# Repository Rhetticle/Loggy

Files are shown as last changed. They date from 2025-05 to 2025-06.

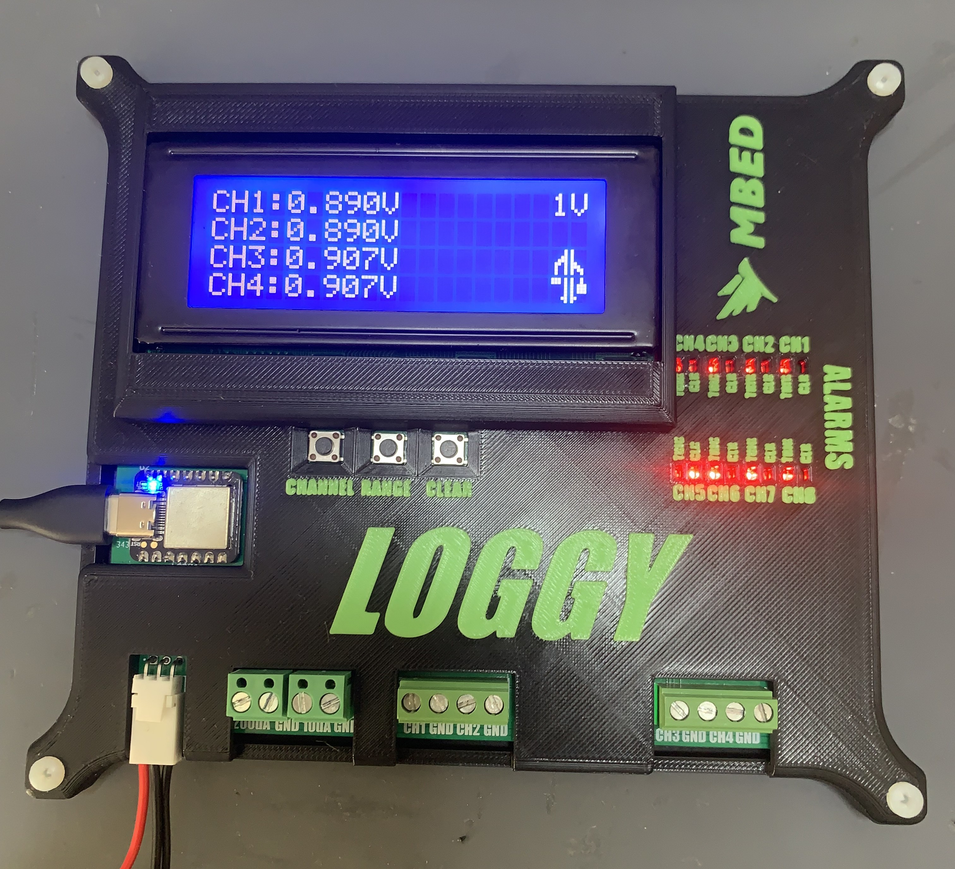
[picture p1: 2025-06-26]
Images/image5.jpeg

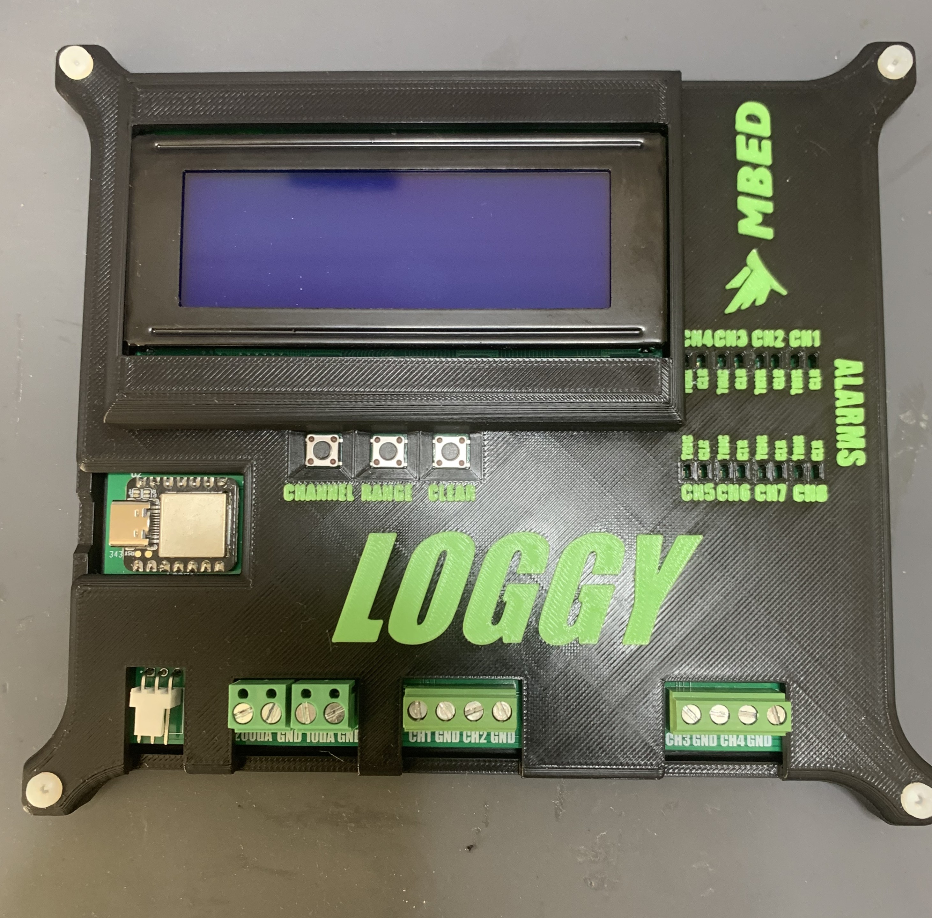
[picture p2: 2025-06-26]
Images/image4.jpeg

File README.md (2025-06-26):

# Loggy
## Four input channel data acquisition device as part of UQ's ENGG2800 Team Project 1 course.



## Overview
Loggy is a four input channel data acquisition device operating at 168 Samples/second with input channels being rated to +/- 12V. Loggy also has four extra channel (CH5 -> CH8) with CH5,CH6,CH7 being the x,y,z acceleration values from the on board accelerometer respectively and CH8 being the ambient temperature. Loggy also features two on board current sources (10uA and 200uA) accurate to +/- 5% for general use (e.g. using with resistive temperature sensors).

Loggy features a simple on board alarm system which monitors the eight channels to see if any go beyond a configurable range (alarm threshold). 16 red LEDs (2 per channel) are used to indicate whether an alarm has occured or not for a given channel. Loggy allows alarms to be in one of three modes; disabled, live (alarm status updated repeatedly) or latching (triggered LED stays latched permenantly once threshold is breached). 

As part of the project a complete GUI was required which would interface to the device via USB to allow users to view live data from their computer as well as configure the device (See "Software" section below for more info). All measurements made by Loggy are also shown on a 20x4 LCD along with alarm statuses and range setting.

## Standards and Requirements
The Loggy device and software was required to comply with mock standards (known as "TP-Standards") to mimic real-world standard compliance. All teams were required to comply with 152 individual standards relating to things such as PCB layout and design, schematic layout and design, software design etc.

The Loggy device and software also had multiple extra requirements on top of the TP-Standards. These requirements included:

* All input channels must be rated for +/- 11V regardless of the range setting
* The entire device must have a BOM of $100 or less
* The GUI must never crash
* Current sources must be accurate to +/- 5%
* Input channel readings must be accurate to +/- 2.5%
* ADCs used must be 16-bit resolution or higher
* All eight channels must be sampled within a 100ms window
* Sample rate must be at least 2 Samples/second

## Hardware
All hardware design was done by Rhett Humphreys. This included designing the digital sections of the device such as the ADCs, MCU, alarm LED driver etc. as well as the analog sections such as the input circuitry for the four input channels. It also included the layout, routing and assembly of the PCB.

The PCB is a standard 2 layer board 1.6mm thick with a 3V3 pour on the top layer and a GND pour on the bottom layer. Surface mount components were preferred in order to stay under the $100 BOM limit. 

## Firmware
Firmware was written by Zhe Gao. This included writing low level drivers for on board devices such as the ADCs, accelerometers and LED driver for alarms as well combining these drivers within the application code for Loggy.

## Software
The GUI software was jointly written by Luke Pidgeon and Sithika Mannakkara. The GUI was written in python and allows the user to view live plots of data read by Loggy as well as configure parameters of the device such as alarm thresholds and alarm types.
### Controls
The controls panel allows the user to connect to the Loggy device as well as perform other actions such as enabling/disabling different plots, changing the voltage range and choosing to begin recording data.
GUI Controls
### Settings
The settings panel allows the user to configure parameters stored on the Loggy device itself such as alarm thresholds and alarm types as well as other GUI parameters such as number of sample points to use for plots, plot scale etc. It also allows the user to configure a voltage channel to be used as a resistive temperature device (RTD) mode.
GUI Settings
### Plots
The plots panel shows the current live plots and allows user to read sampled value by hovering their mouse over the plots
GUI Plots
### Replay
The replay panel allows users to replay/view a data recording previously made. Recorded data is saved as a csv file which can then be imported into the GUI for viewing and also allows users to view the value of samples similar to the live plots.
GUI Replay

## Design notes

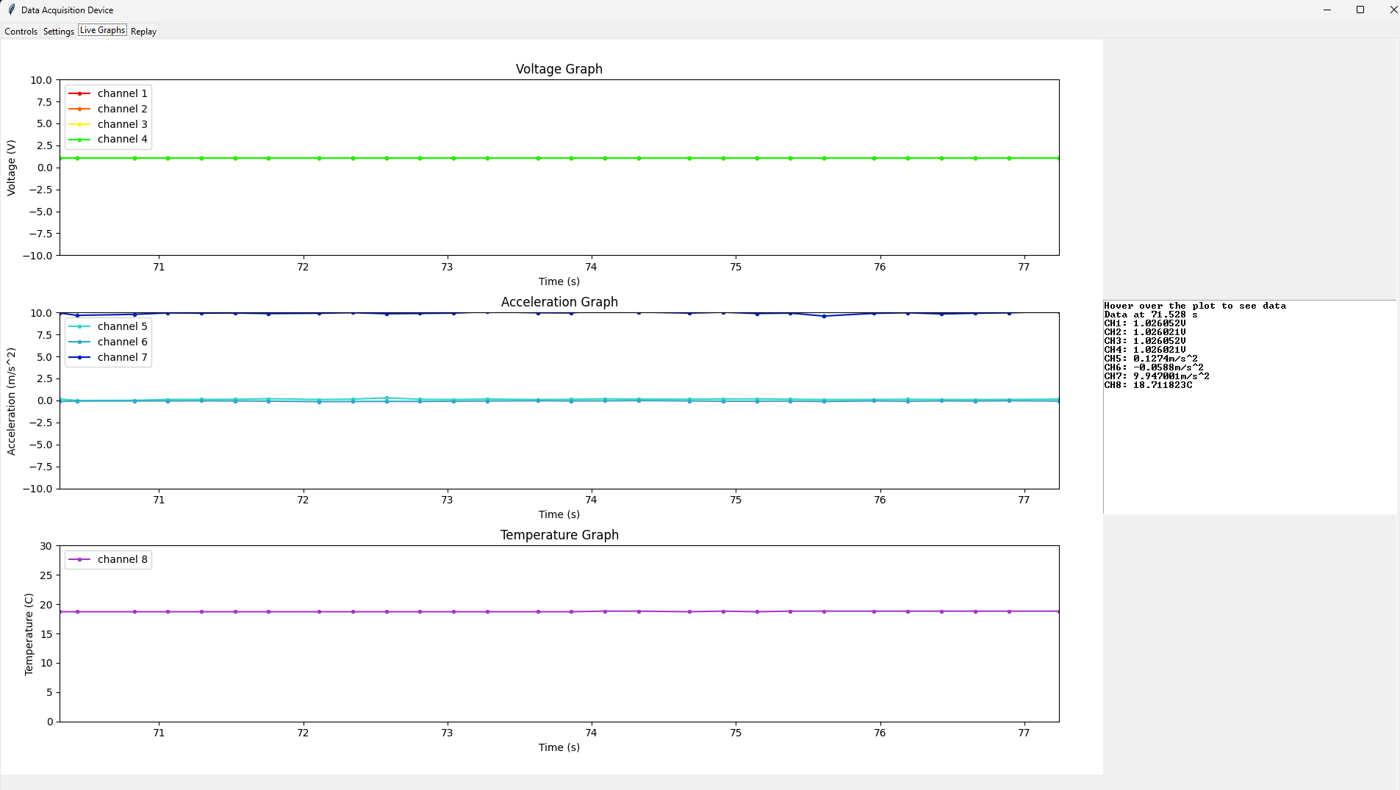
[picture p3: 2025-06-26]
Images/GUI Plots.png

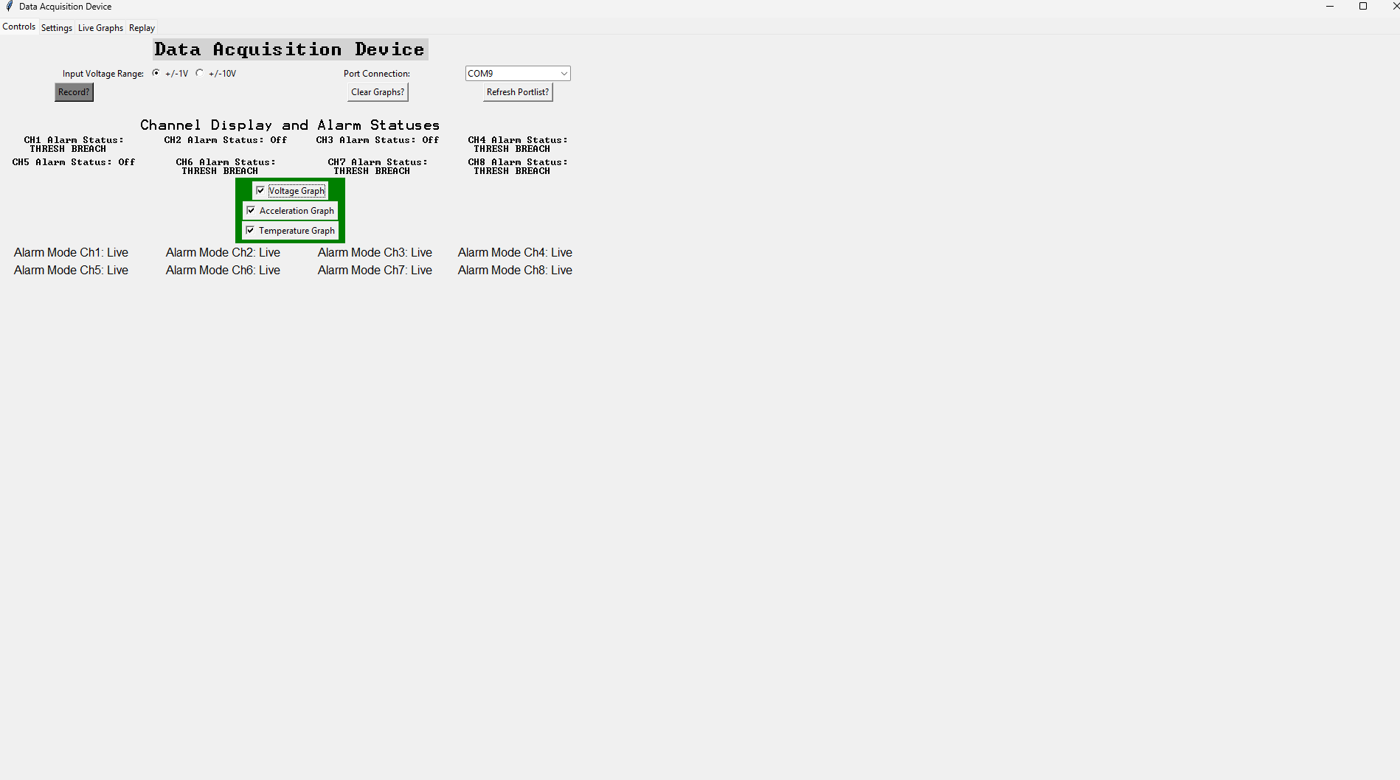
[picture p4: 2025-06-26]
Images/GUI Controls.png

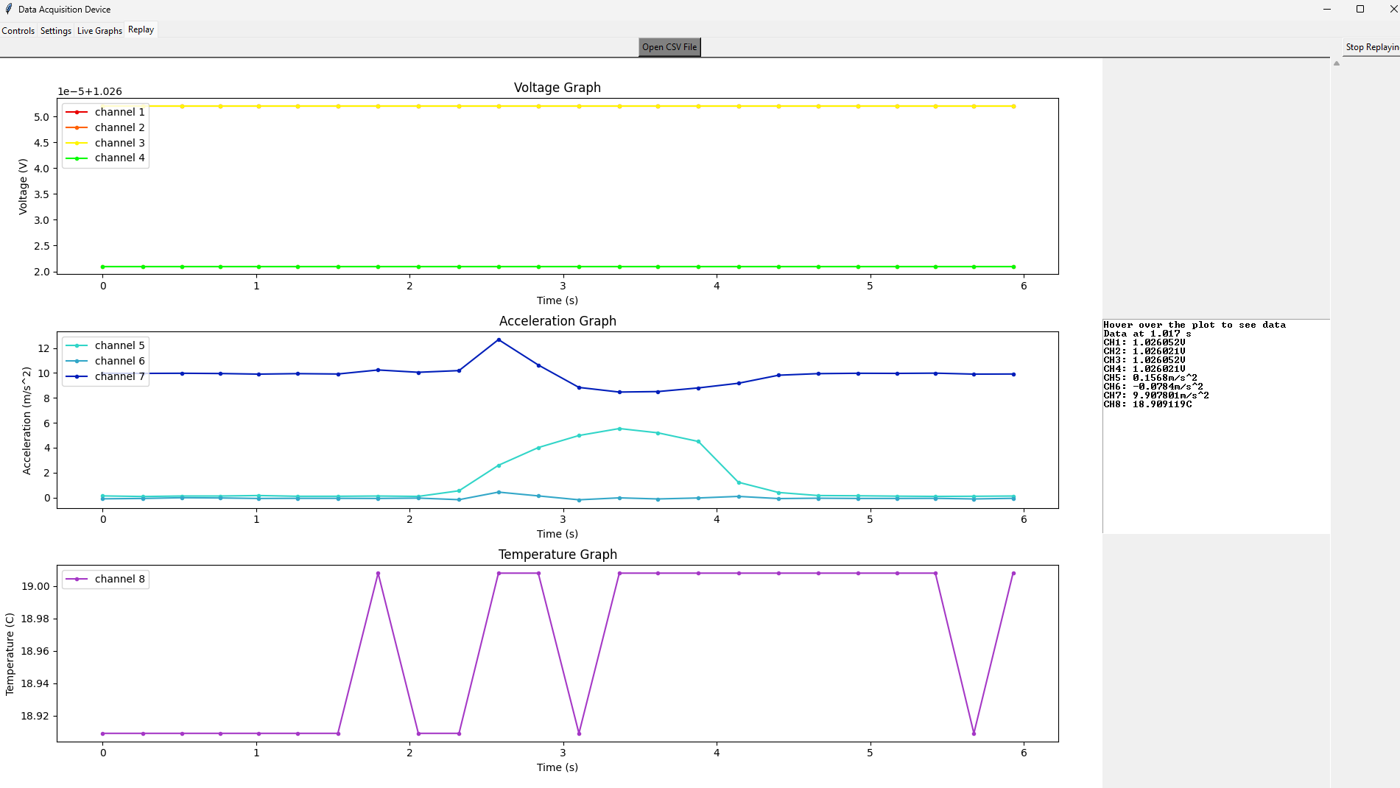
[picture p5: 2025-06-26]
Images/GUI Replay.png

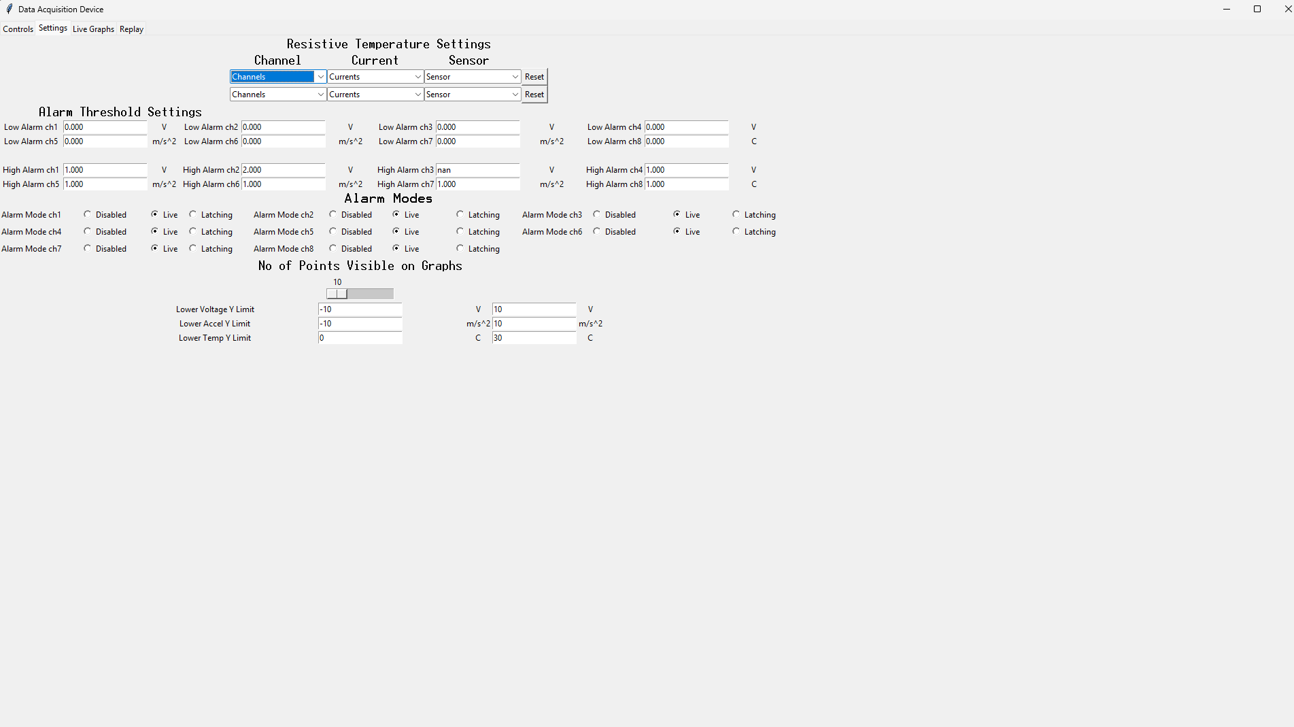
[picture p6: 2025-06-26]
Images/GUI Settings.png

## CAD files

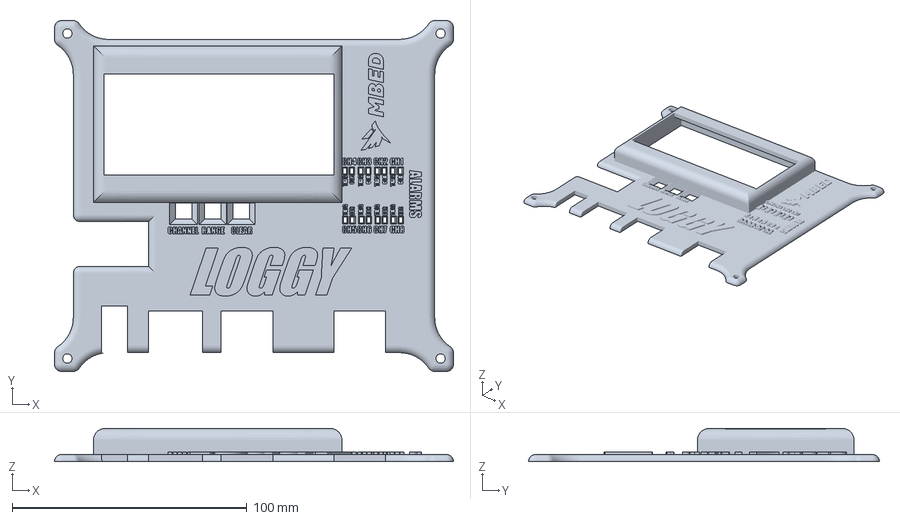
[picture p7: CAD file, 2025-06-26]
STL/Loggy Top Proj.3mf
170.0 x 149.5 x 14.1 mm

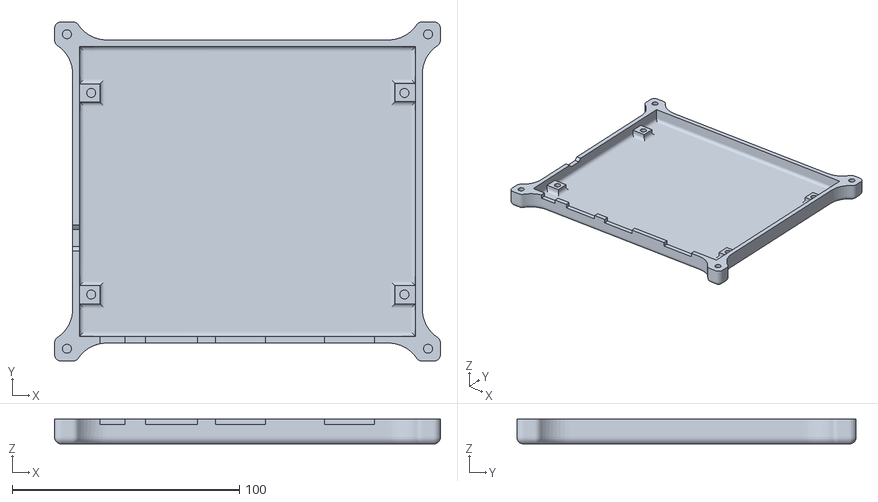
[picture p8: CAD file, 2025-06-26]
STL/Loggy Bottom.stl
170.0 x 149.5 x 11.0

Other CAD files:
STL/Loggy Top.stl

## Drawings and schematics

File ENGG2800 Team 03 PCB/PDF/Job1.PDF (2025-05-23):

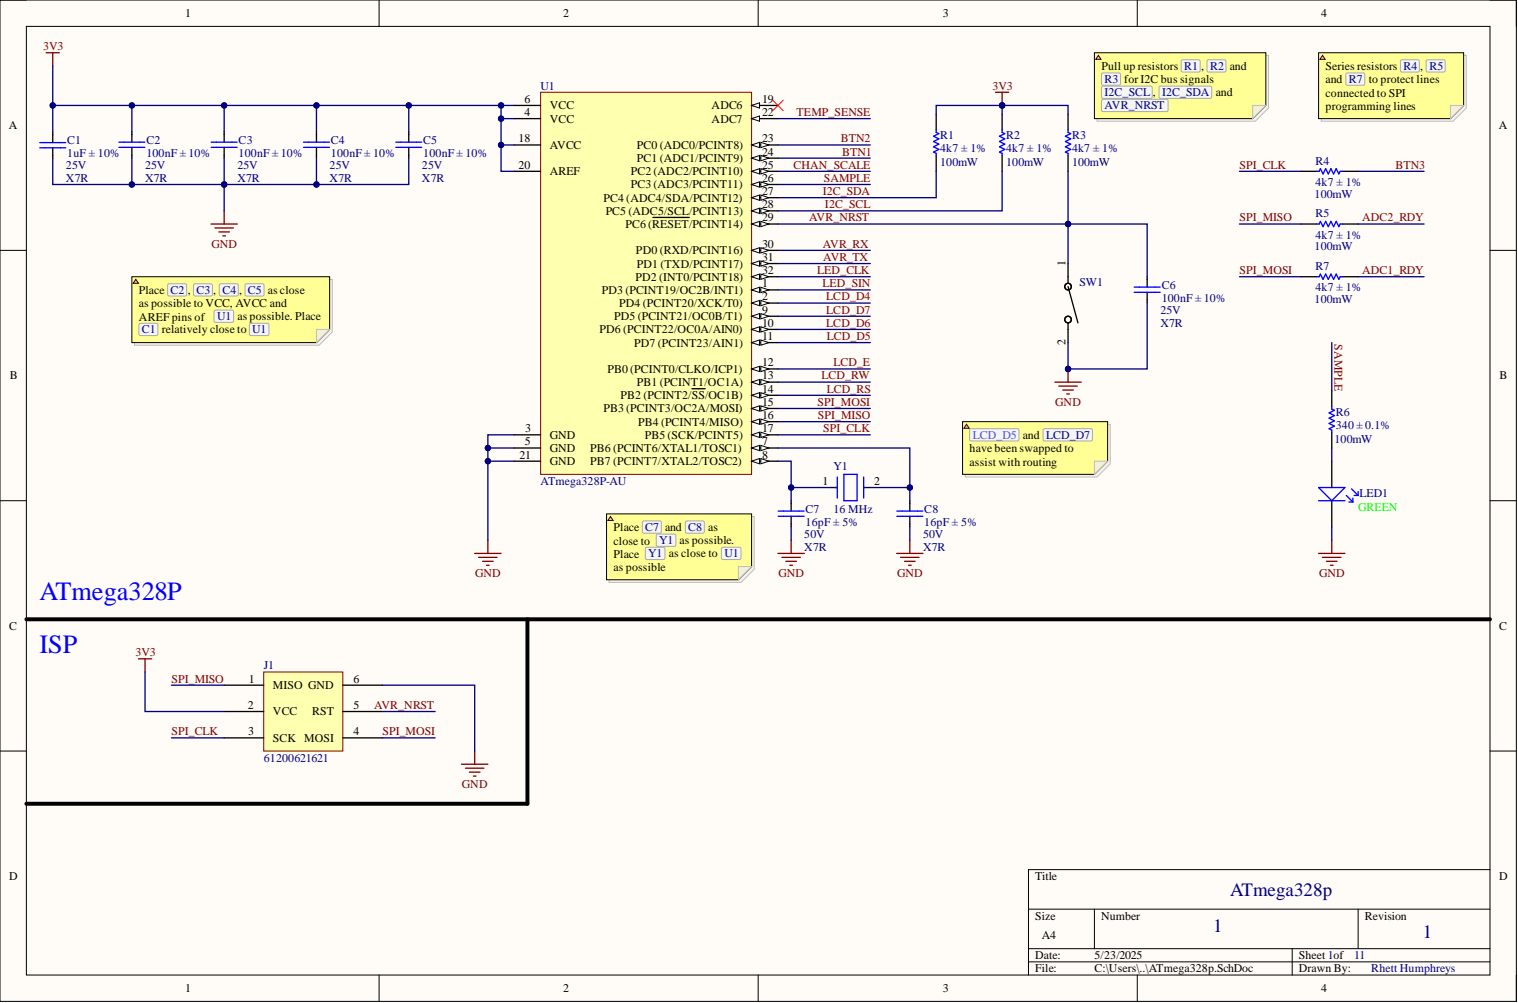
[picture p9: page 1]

2 6 2 7 | SAMPL E I2C_ S D A

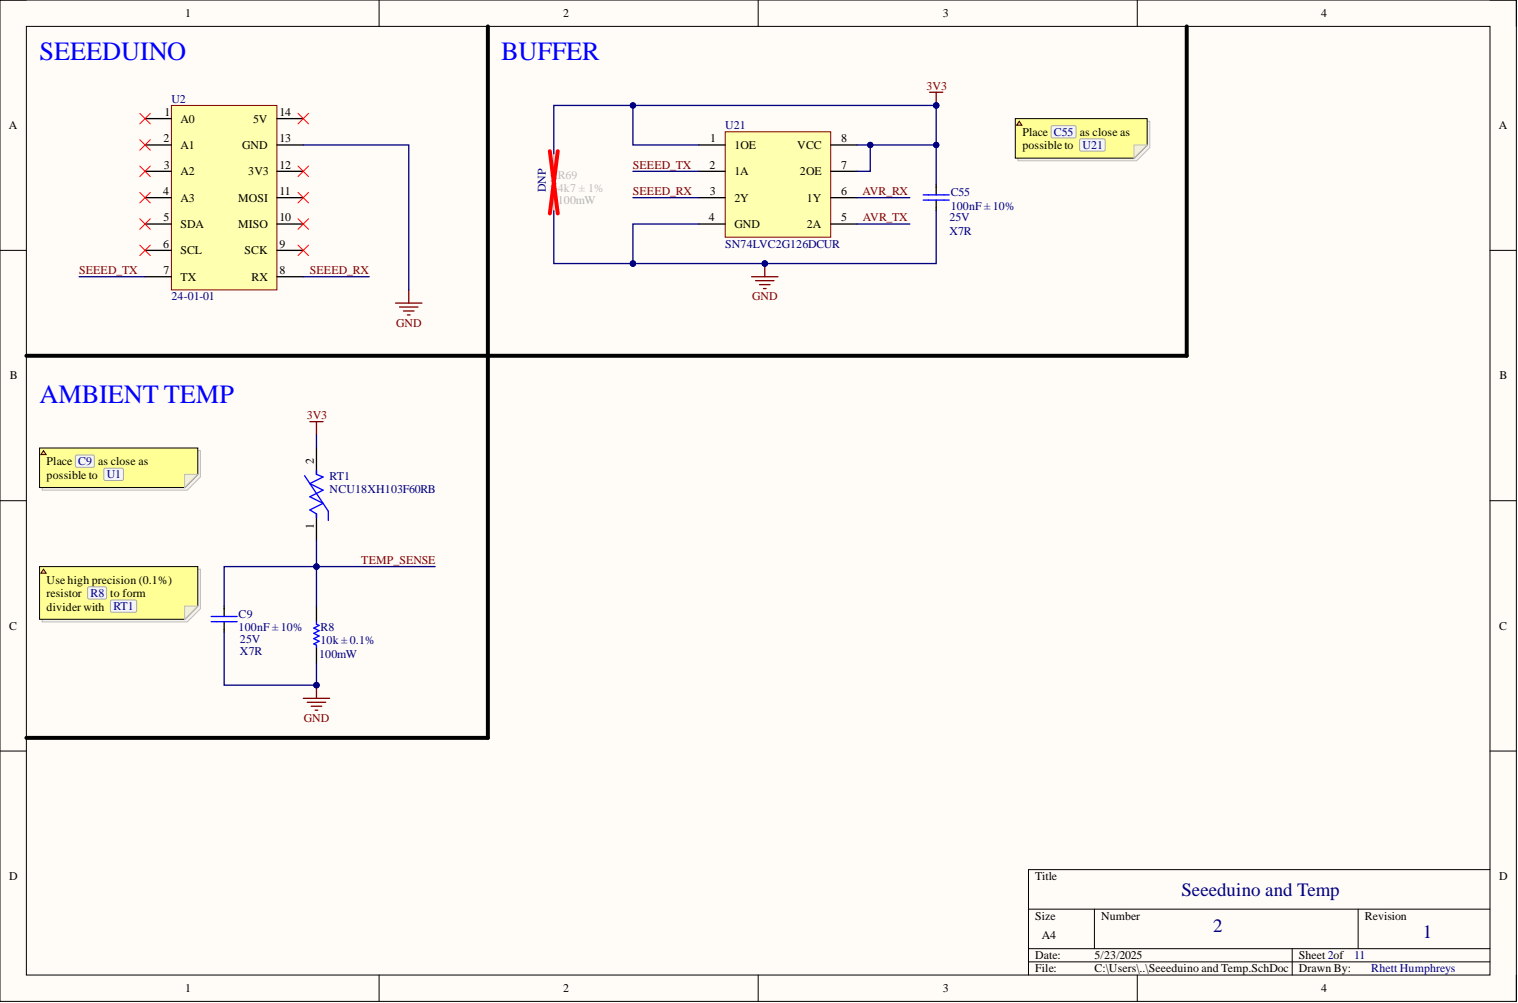
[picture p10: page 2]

Place C55 as close as
possible to U21

Place C9 as close as
possible to U1

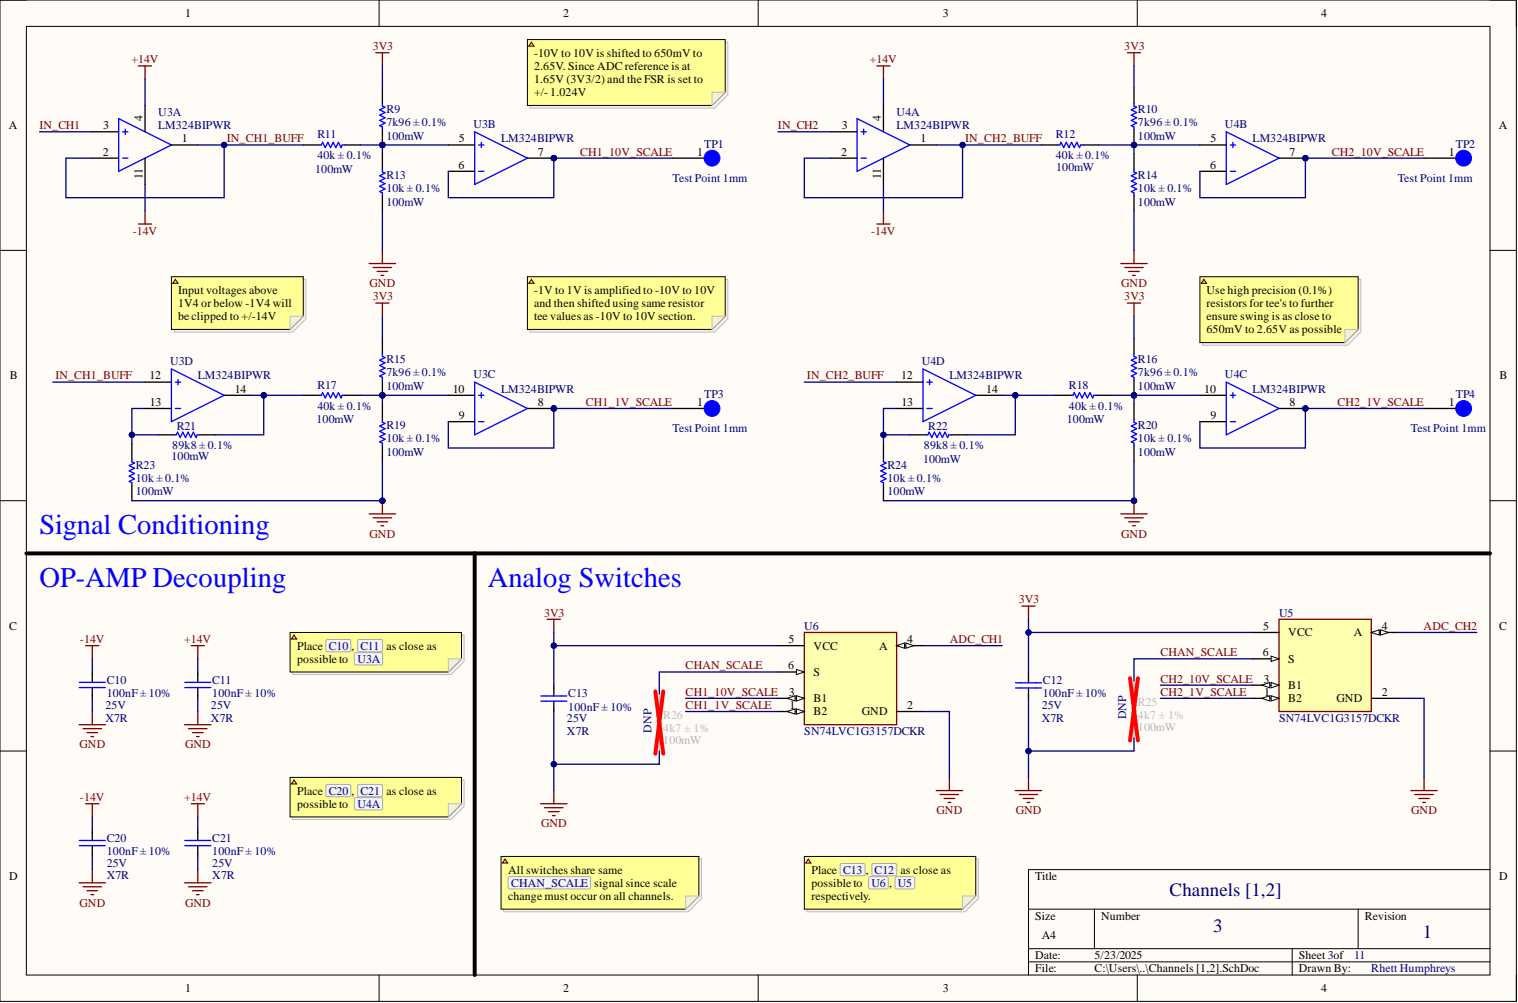
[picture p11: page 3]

-10V to 10V is shifted to 650mV to
2.65V. Since ADC reference is at
1.65V (3V3/2) and the FSR is set to

-1V to 1V is amplified to -10V to 10V
and then shifted using same resistor
tee values as -10V to 10V section.

Use high precision (0.1%)
resistors for tee'sto further
ensure swing is as close to
650mV to 2.65V as possible

Place C10 , C11 as close as
possible to U3A

Place C20 , C21 as close as
possible to U4A

All switches share same
CHAN_SCALE signalsince scale
change must occur on all channels.

Place C13 , C12 as close as
possible to U6 , U5
respectively.

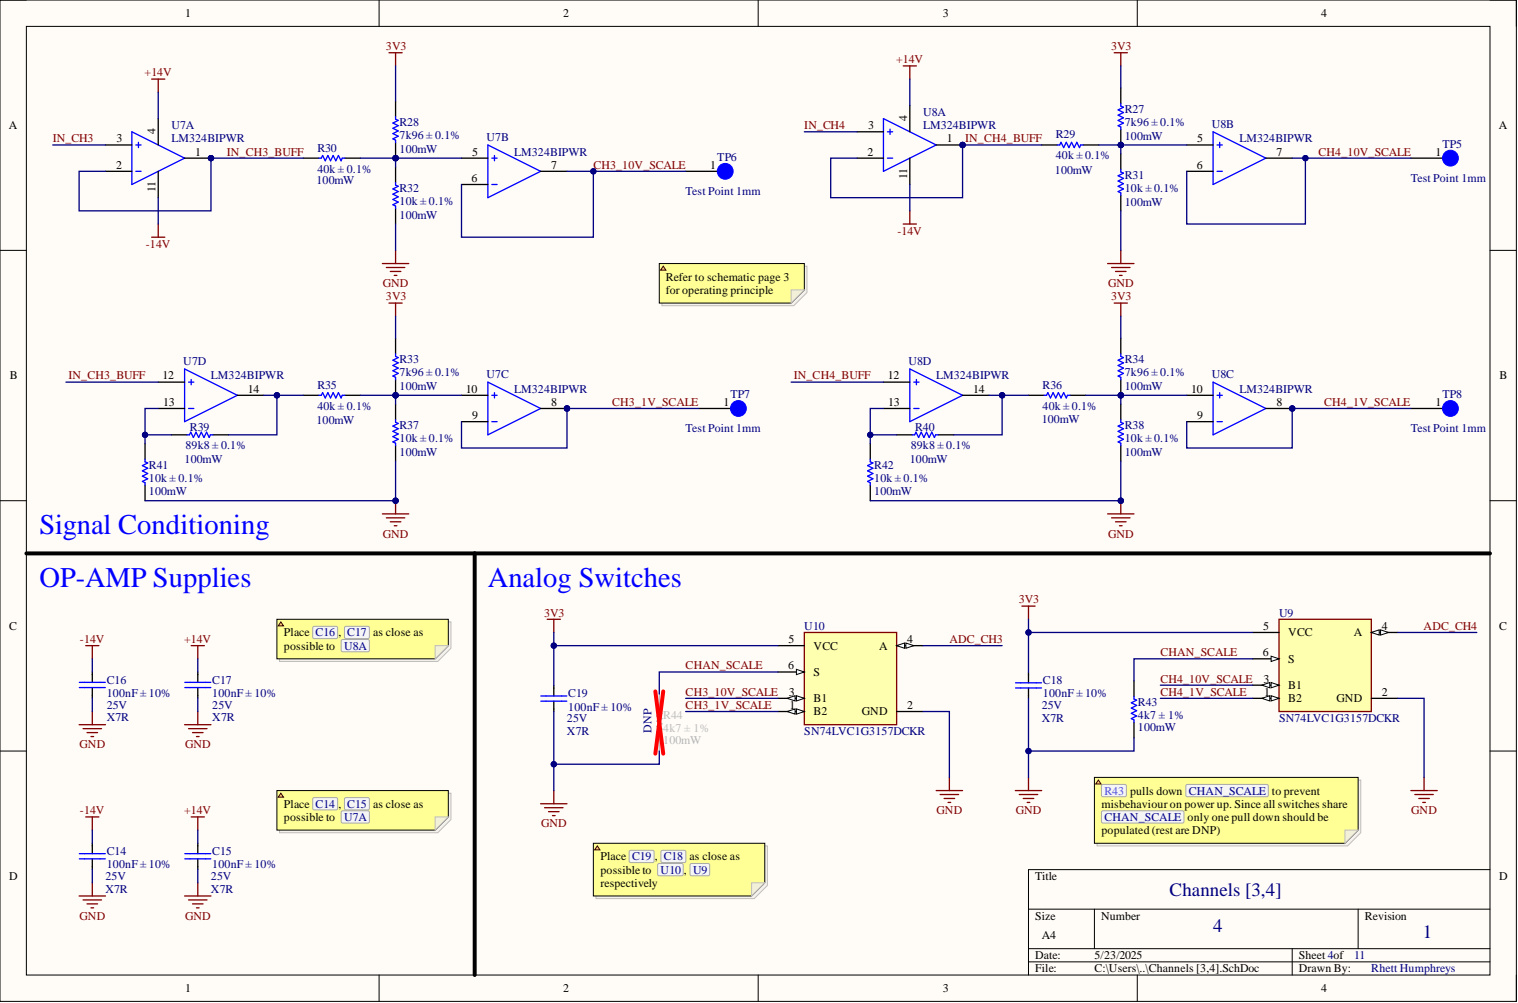
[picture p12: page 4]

Refer to schematic page 3
for operating principle

Place C16 , C17 as close as
possible to U8A

R43 pulls down CHAN_SCALE to prevent
misbehaviour on power up. Since all switches share
CHAN_SCALE only one pull down should be
populated (rest are DNP)

Place C14 , C15 as close as
possible to U7A

Place C19 , C18 as close as
possible to U10 , U9
respectively

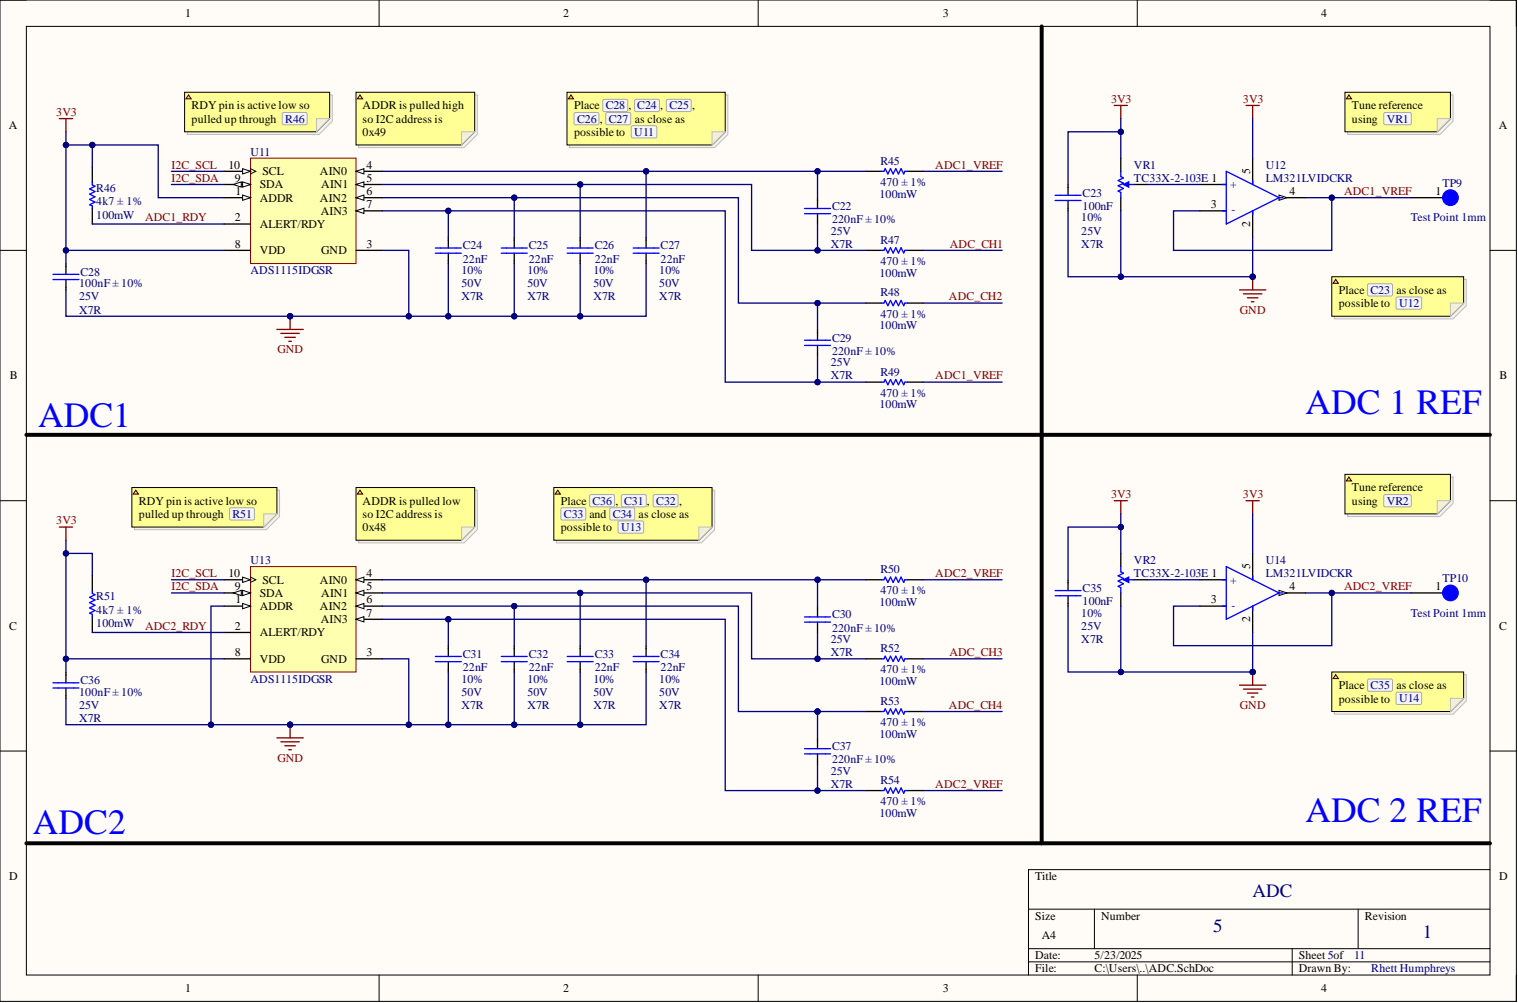
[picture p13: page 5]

I2C_SCL I2C_ S D A R4 6

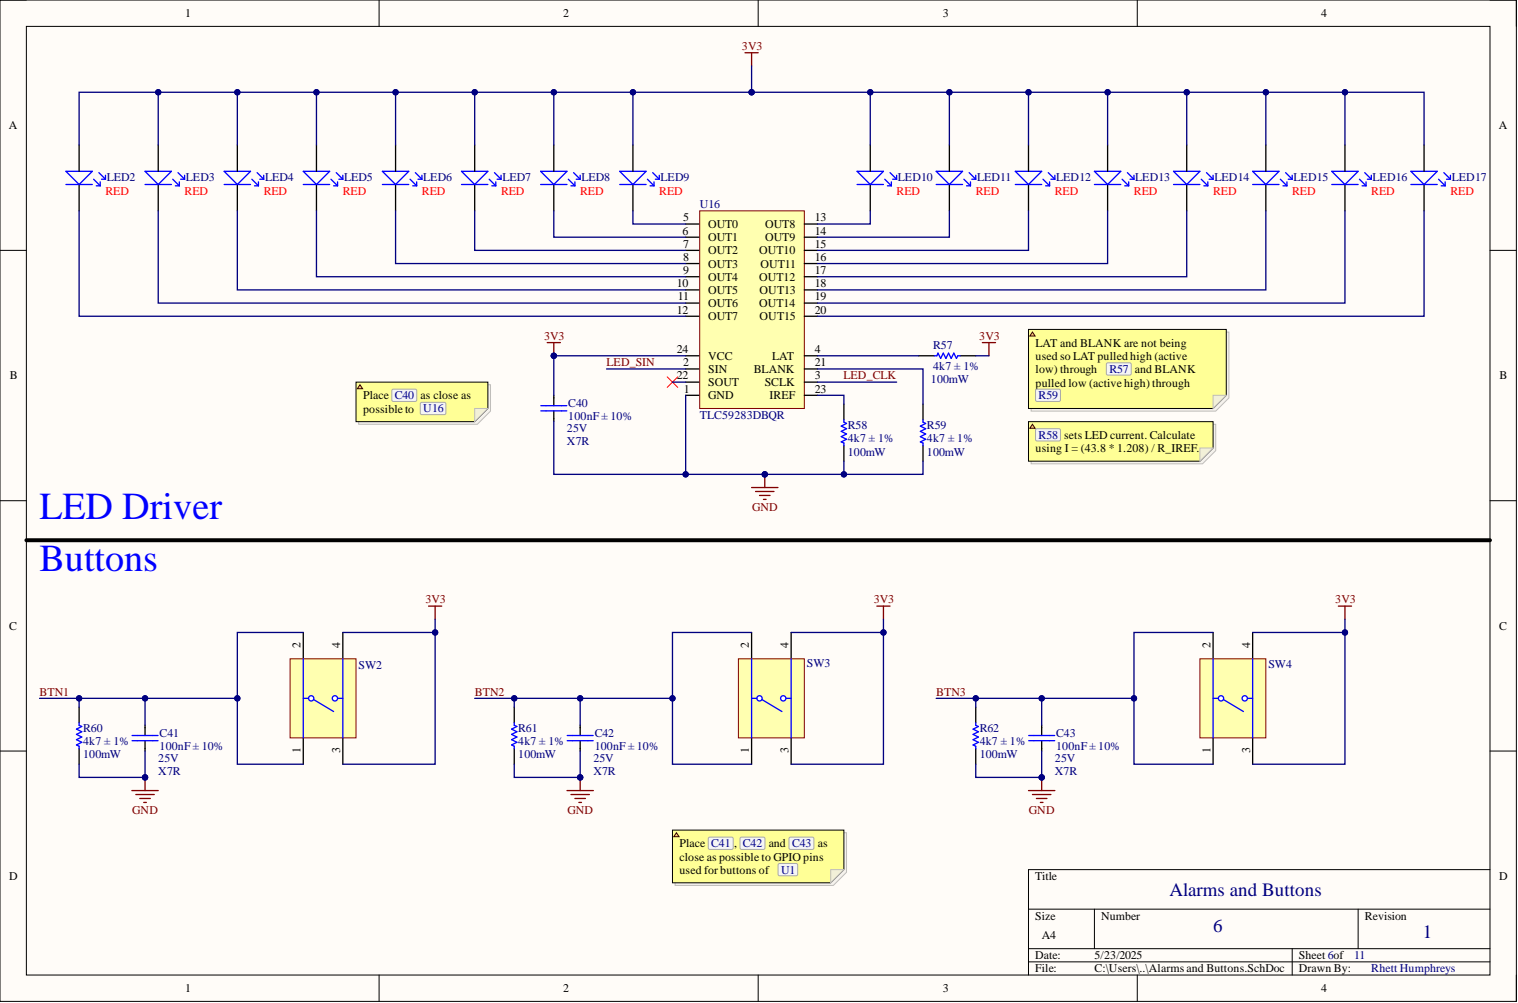
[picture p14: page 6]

LAT and BLANK are not being
used so LAT pulled high (active
low) through R57 and BLANK
pulled low (active high) through

Place C40 as close as
possible to U16

R58 sets LED current. Calculate
using I = (43.8 * 1.208) / R_IREF.

Place C41 , C42 and C43 as
close as possible to GPIO pins
used for buttons of U1

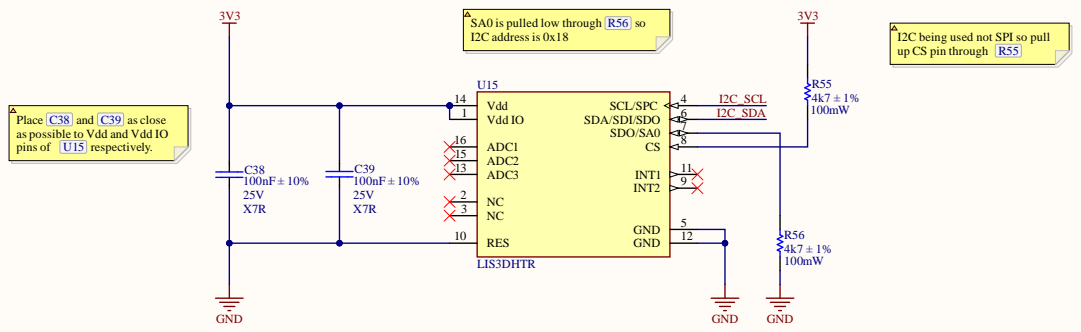
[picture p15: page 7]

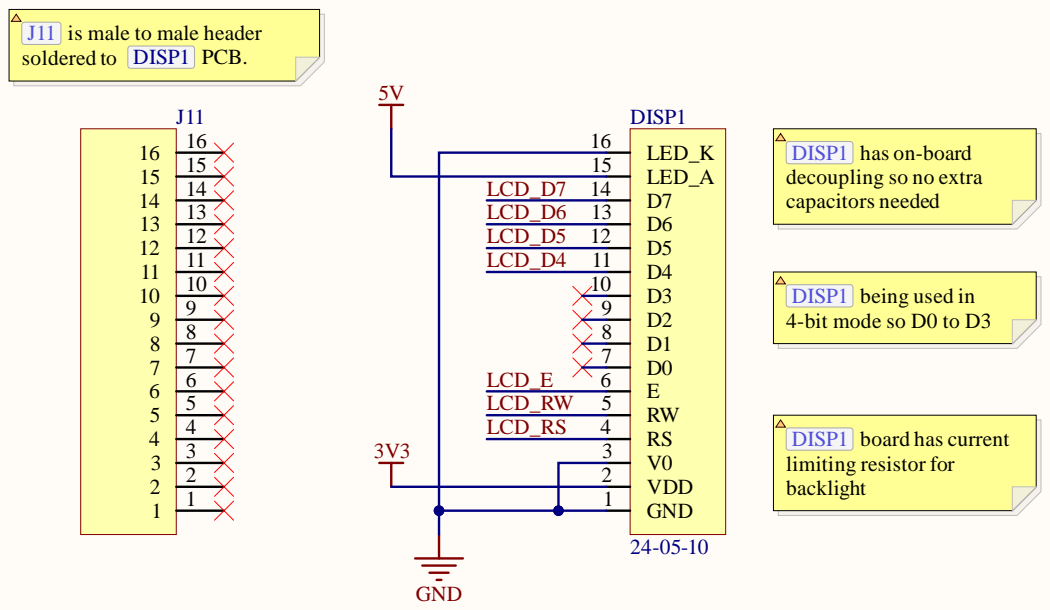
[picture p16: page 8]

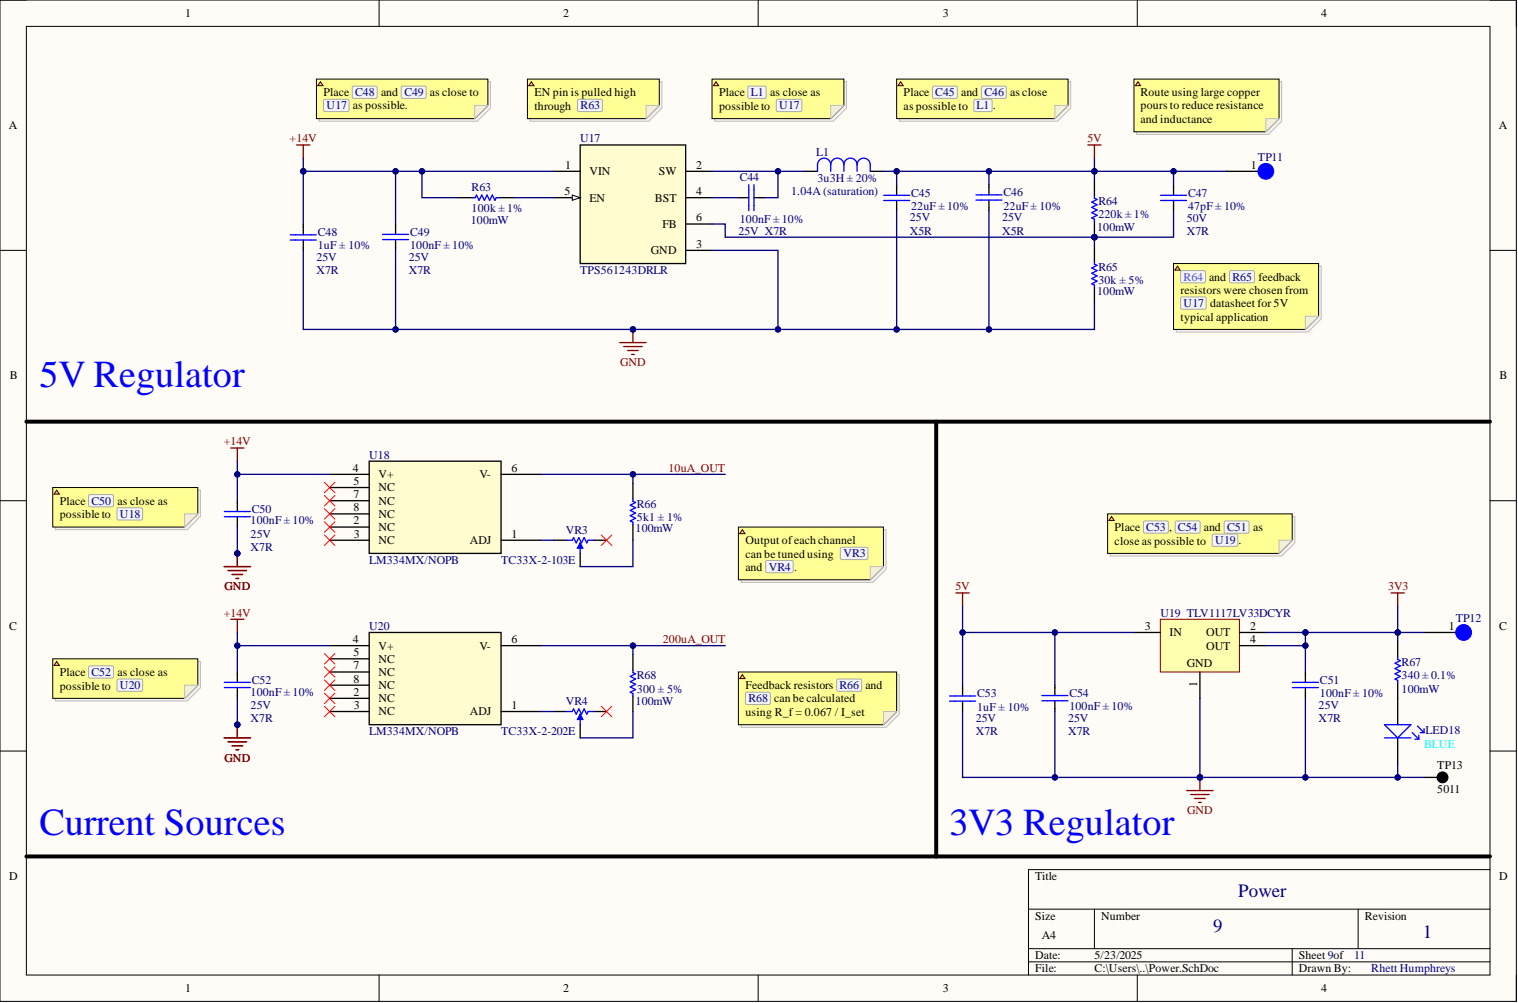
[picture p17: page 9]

Place C48 and C49 as close to
U17 as possible.

EN pin is pulled high
through R63

Place L1 as close as
possible to U17

Place C45 and C46 as close
as possible to L1 .

Route using large copper
poursto reduce resistance
and inductance

R64 and R65 feedback
resistors were chosen from
U17 datasheet for 5V
typical application

Place C50 as close as
possible to U18

Place C53 , C54 and C51 as
close as possible to U19 .

Output of each channel
can be tuned using VR3
and VR4 .

Place C52 as close as
possible to U20

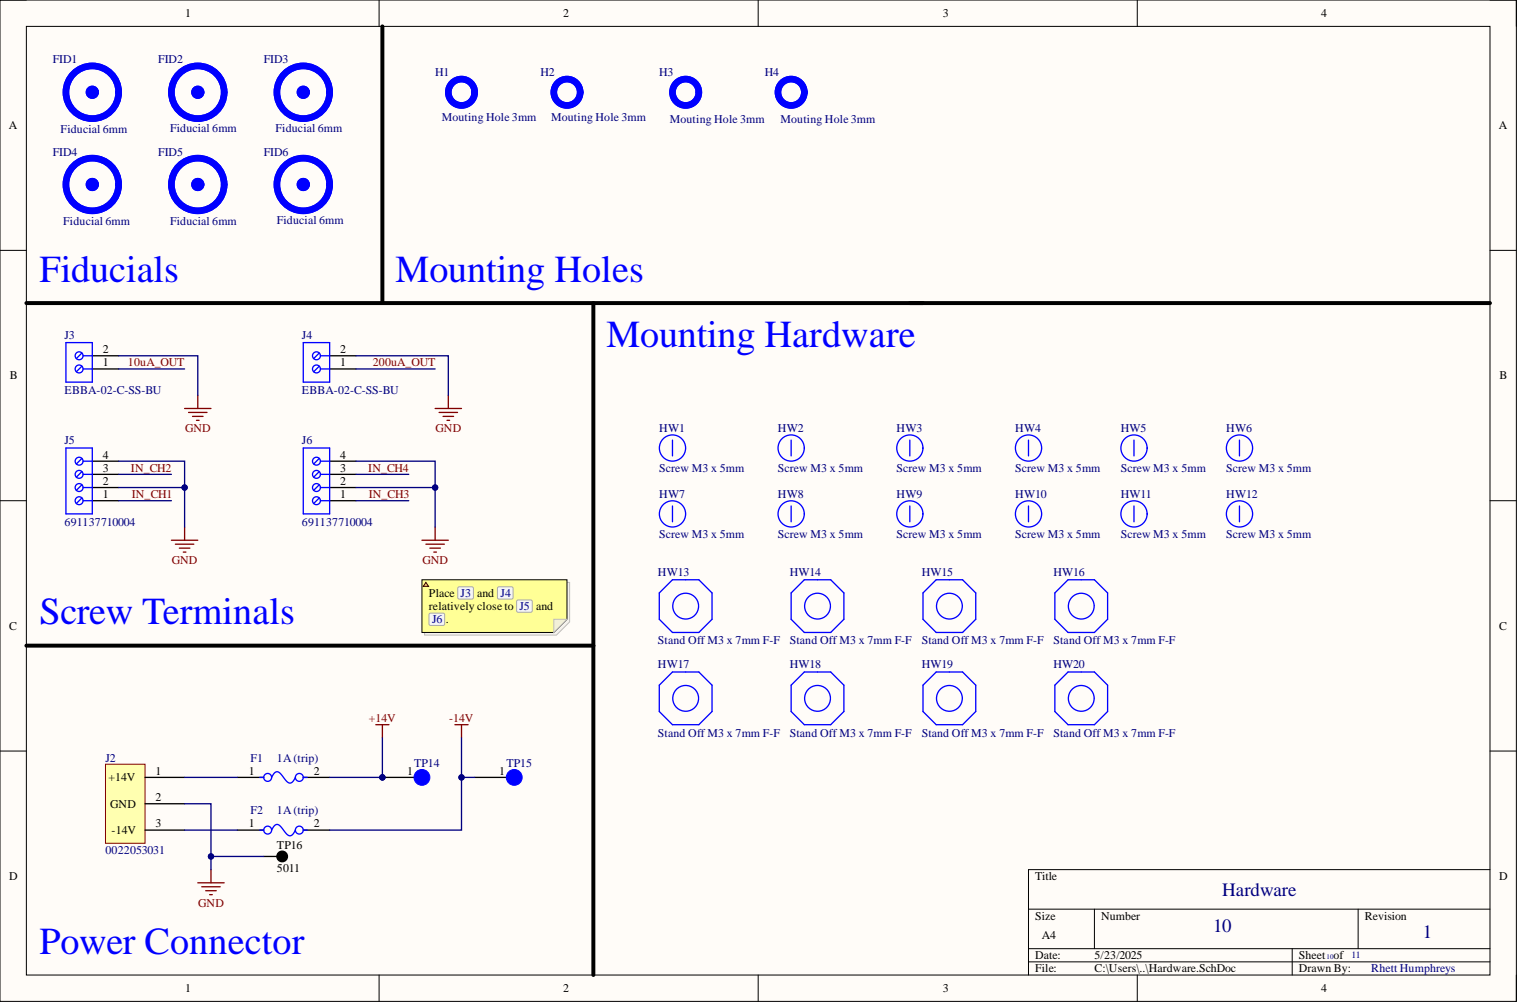
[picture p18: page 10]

Place J3 and J4
relatively close to J5 and

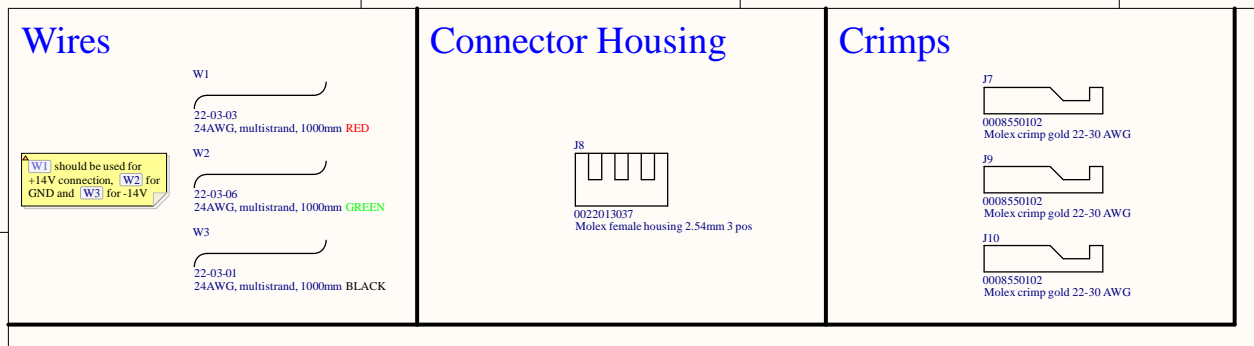
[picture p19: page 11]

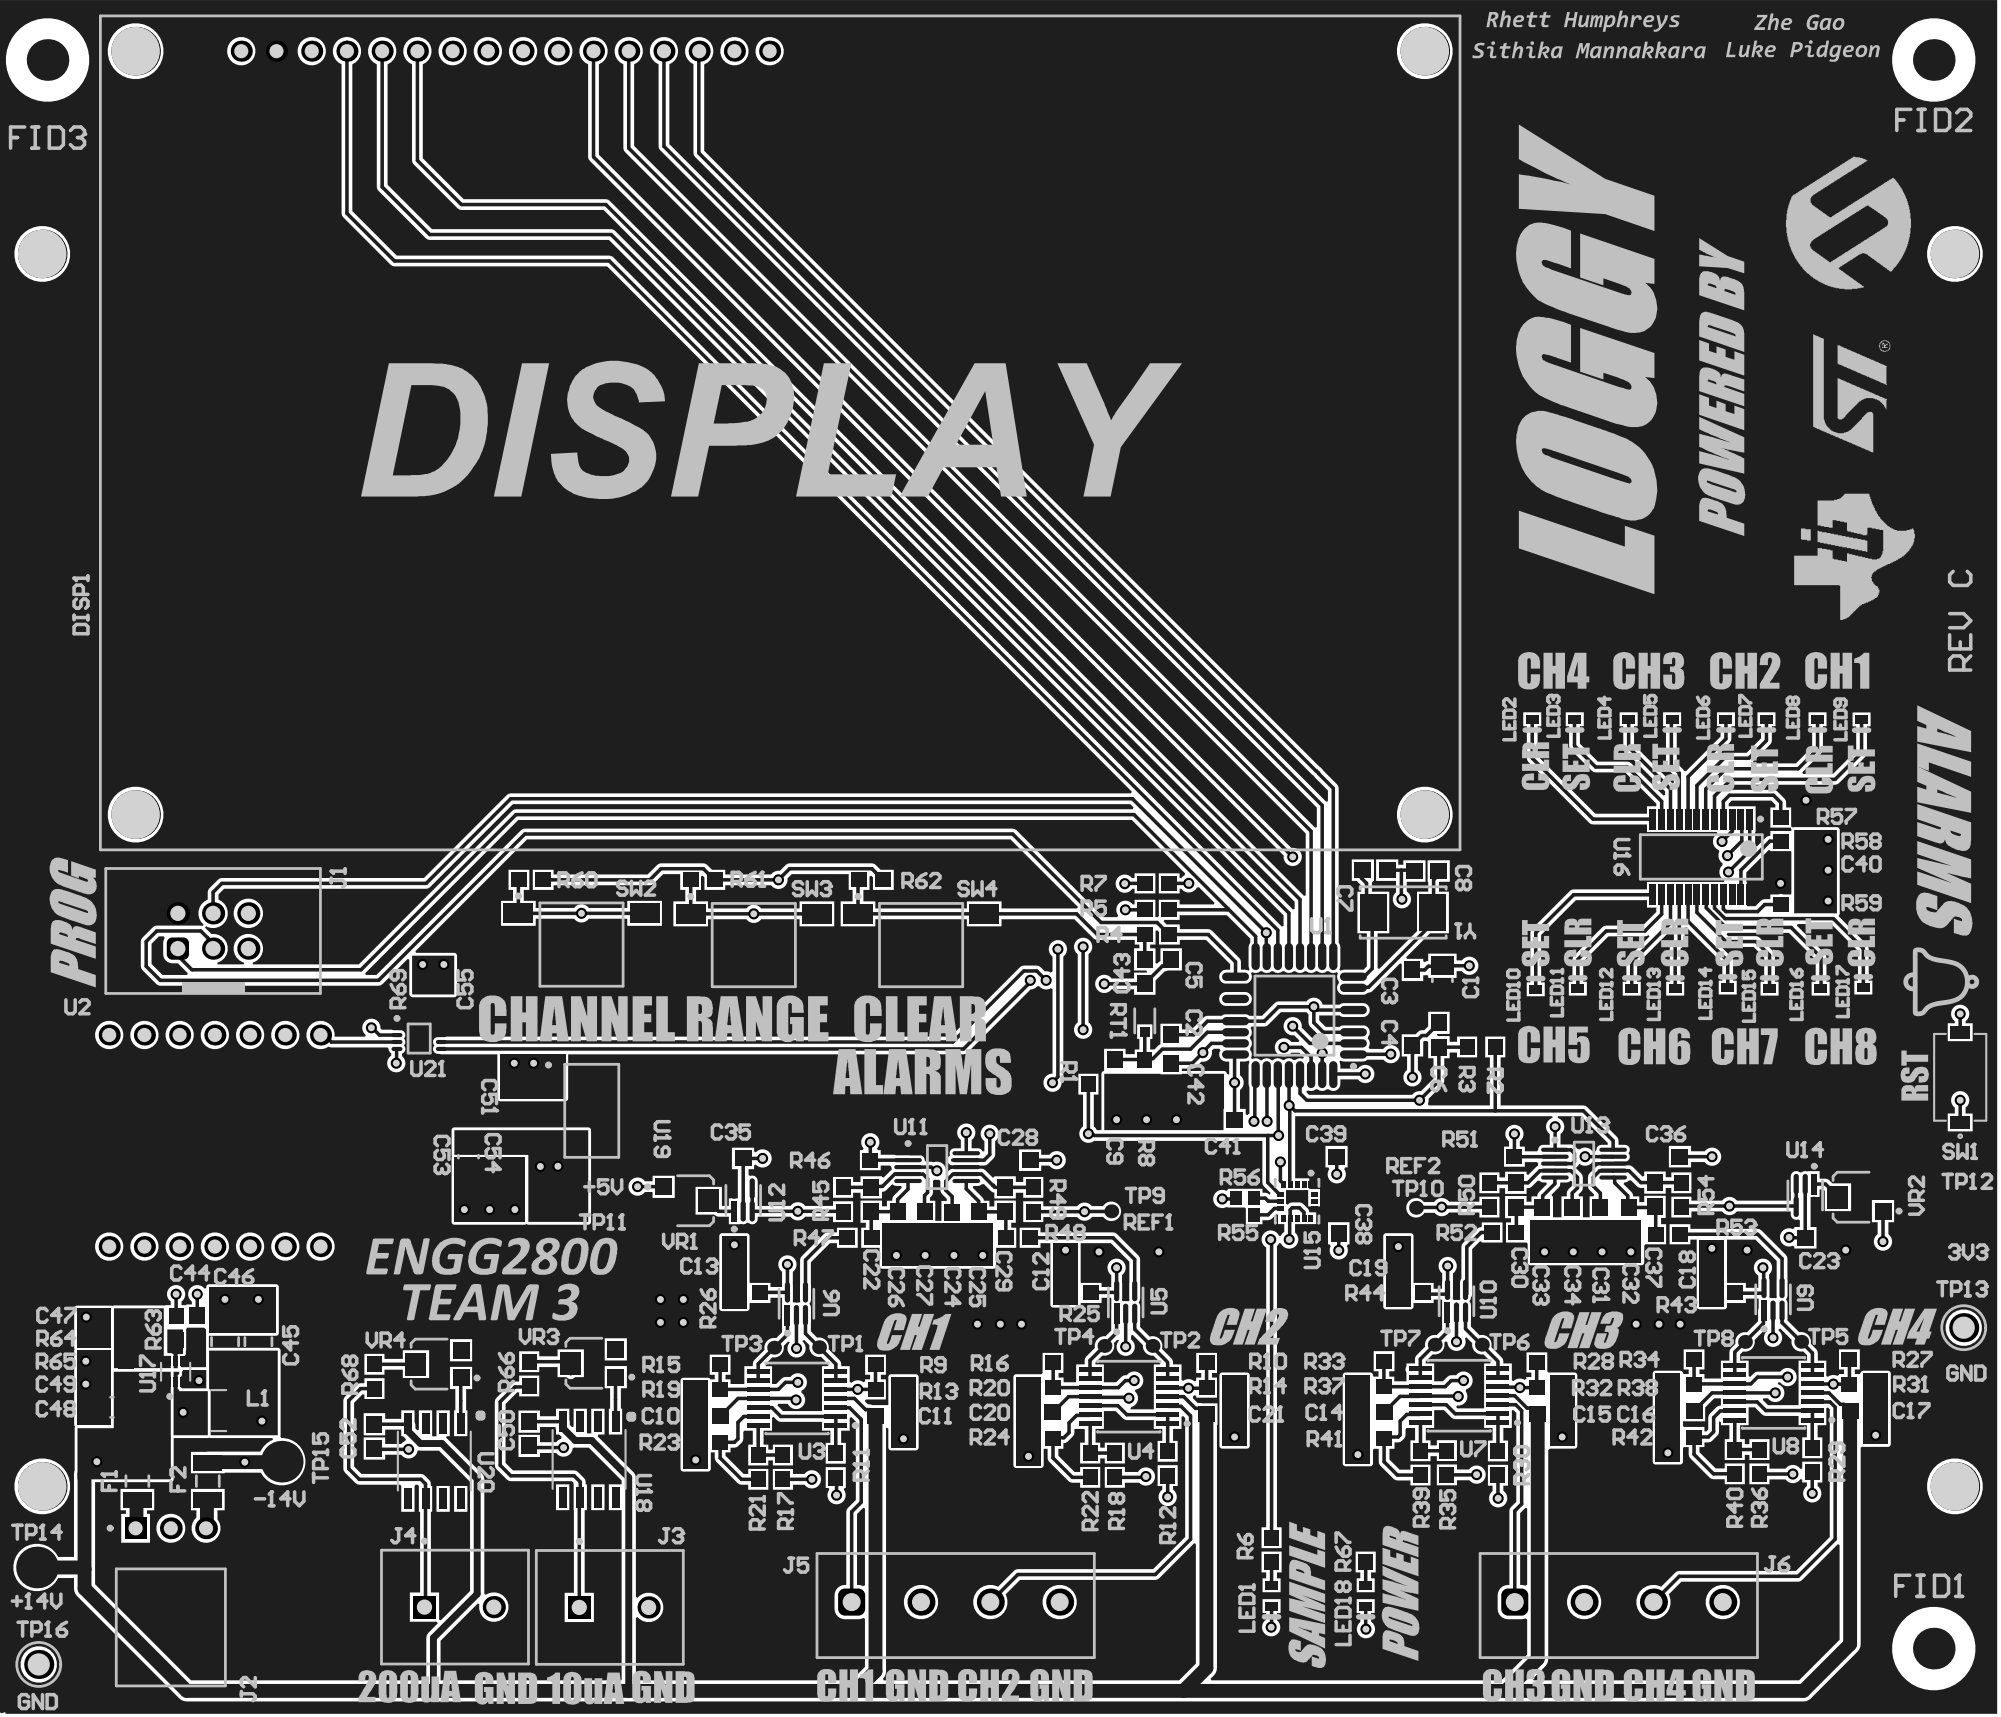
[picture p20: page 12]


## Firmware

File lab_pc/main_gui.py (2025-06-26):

"""
Team 3 Data Acquisition Device GUI Software
Version 1.5
- Text box

This program will be able to display input from the loggy.
It will be able to change settings in the loggy.
"""
import csv
import math
import os
import tkinter as tk
import tkinter.ttk as ttk
from tkinter import filedialog
import numpy as np
from matplotlib import pyplot as plt, animation
from matplotlib.backends.backend_tkagg import FigureCanvasTkAgg
import serial as ser
import serial.tools.list_ports as stlp
import serial.threaded as st
from datetime import datetime
import sys
import time
import threading as th
import queue as qu

VRWIDG = 0
LOWATWIDG = 1
HIGHATWIDG = 2
ALARMMODEWIDG = 3
ALARMMODELABEL = 4
ALARMSTATUSLABEL = 5

STARTCONTMESSAGE = "START CONT#"
GUI_FONT = "Terminal"

ON = 1
OFF = 0
LOWER_SOS = 1
UPPER_SOS = 2

ONEV = 0
TENV = 1
DISABLED = 0
LIVE = 1
LATCHING = 2
THERMISTOR = 2
PT1000 = 3
LOWI = 4
HIGHI = 5
DIGIT = 1
FLOAT = 0
POSITIVE = 1
NEGATIVE = 2
BAUDRATE = 9600
READIN = 255
# Constants for the thermistor
A_THERM = 3.354016e-3
B_THERM = 2.909670e-4
C_THERM = 1.632136e-6
D_THERM = 7.192200e-8
# Rtemp related constants
CHANNELS_RTEMP = ("Channels", "CH1", "CH2", "CH3", "CH4")
CURRENTS_RTEMP = ("Currents", "200uA", "10uA")
SENSOR_RTEMP = ("Sensor", "Thermistor", "PT1000")
# Channels in the loggy
CHANNELS_LIST = (1, 2, 3, 4, 5, 6, 7, 8)
VOLT_CHANNELS = (1, 2, 3, 4)
ACCEL_CHANNELS = (5, 6, 7)
TEMP_CHANNEL = 8
# Plot related constants
TEXT_BOX_STRING = "Hover over the plot to see data\n"
LIVE_PLOT_INTERVAL = 250
PLOT_HEIGHT = 10  # The dimensions of the plot
PLOT_WIDTH = 15  # These values are best for 1920 x 1080 displays
LEGEND_LOC = "upper left"
VOLT_Y_LABEL = "Voltage (V)"
ACCEL_Y_LABEL = "Acceleration (m/s^2)"
TEMP_Y_LABEL = "Temperature (C)"
X_LABEL = "Time (s)"
V_TITLE = "Voltage Graph"
A_TITLE = "Acceleration Graph"
T_TITLE = "Temperature Graph"
V_GRAPH_IDX = 0
A_GRAPH_IDX = 1
T_GRAPH_IDX = 2
COLOURS = ("#e90000", "#ff6100", "#fff500", "#05fb00",
           "#31d5c8", "#33a7c8", "#001eba", "#a538c6")
MARKER = "."
# File related constants
FILE_TYPES = (('CSV files', '*.csv'),)
FILENAME_FORMAT = "%Y-%m-%d_%H-%M-%S"

# global variable semaphor for threading.
lock = th.Lock()
errors = qu.Queue()


def make_error_pannel(control_frame: tk.Frame | tk.Tk, message: str,
                      program_running: bool):
    """
    Function make an error pannel according to the specific error that has
    occured to the user.
    Parameters
    ----------
    control_frame: tk.Frame|tk.Tk
        Frame or window in which error message is being built from.
    message: str
        Error message to be displayed.
    program_running: bool
        Boolean indicates whether GUI is running.
    Returns nothing.
    """
    if program_running:
        lock.acquire()
        sys.stdout.write("Making top level: \n")
        error_pannel = tk.Toplevel(control_frame)
        sys.stdout.write("Made top level: \n")
        error_message = tk.Label(error_pannel, text=message, bg="red")
        error_message.grid()
        lock.release()
    return


class Data:
    """
    The place where all the data is stored.
    Readings from the loggy are stored in a list.
    (Time, ch1, ch2, ch3, ..., ch8)
    """

    def __init__(self, ready_to_plot):
        """
        Parameters
        ----------
        ready_to_plot : int
            1 for ready, 0 for not ready.
        """
        # Temporary place to store data from the loggy.
        # Has a maximum size of 1000.
        self._data_list = [[] for _ in range(9)]
        # The place where data is saved
        self._save_list = [[] for _ in range(9)]
        # Headers are changed when a voltage channel is switched to a rtemp.
        self.headers = ["Time",
                        "CH1 (V)", "CH2 (V)", "CH3 (V)", "CH4 (V)",
                        "CH5 (m/s^2)", "CH6 (m/s^2)", "CH7 (m/s^2)",
                        "CH8 (C)\n"]
        self._ready_to_plot = ready_to_plot
        # The time that the loggy connected to the GUI
        self._start_time = None
        self._is_data_recording = False  # Flag for recording

    def set_headers(self, headers: list) -> None:
        """Function is used to change the headers of Data.
        Only used in the replay graph.
        Returns nothing
        """
        self.headers = headers

    def record(self) -> None:
        """Function is called when user presses record button.
        The data class will begin to record data when this function is called.
        Returns nothing
        """
        self._is_data_recording = True

    def toggle_rtemp_mode(self, channel: int, current: str,
                          sensor: str) -> None:
        """Function is used to change the mode of a Voltage channel
        Channels 1 to 4 can be switched to temperature mode
        if current != "OFF" and sensor != "OFF"
        Channels 1 to 4 can be switched to voltage mode
        if current == "OFF" and sensor == "OFF"
        Returns nothing"""
        if channel in VOLT_CHANNELS:  # only accept voltage channels
            # Checks in case the main rtemp channel checkbutton was clicked
            # off.
            if current == "OFF" and sensor == "OFF":
                self.headers[channel] = f"CH{channel} (V)"
                return
            self.headers[channel] = f"CH{channel} (C) {current} {sensor}"

    def save_data(self) -> None:
        """Saves the recorded data to a csv file.
        Line format: YYYY-MM-DD_HH-MM-SS.sss,CH1,CH2,CH3,CH4,CH5,CH6,CH7,CH8
        file name format: YYYY-MM-DD_HH-MM-SS.csv
        The file will be saved to the usb drive.
        """
        if not self._save_list:
            return  # _save_list is empty
        start_time = datetime.fromtimestamp(self._save_list[0][0])
        # create the filename string
        filename = start_time.strftime(FILENAME_FORMAT) + ".csv"
        file_directory = os.getcwd()  # current working directory
        file_path = os.path.join(file_directory, filename)
        file = open(file_path, "w")
        print(f"Saved to {file_path}")
        # Write the headers on the first line
        file.write(self.headers[0])
        for header in self.headers[1:]:
            file.write(f",{header}")
        # Write the data that was recorded
        for i in range(len(self._save_list[0])):
            time_stamp = self._save_list[0][i]
            dt = datetime.fromtimestamp(time_stamp)
            dt_str = (dt.strftime(FILENAME_FORMAT)
                      + f".{dt.microsecond // 1000:03d}")
            line = f"{dt_str}"
            for channel in range(1, 9):
                line += f",{self._save_list[channel][i]}"
            line += "\n"
            file.write(line)
        file.close()  # close file resources.
        self._save_list = [[] for _ in range(9)]  # reset the _save_list.
        self._is_data_recording = False  # data has stopped recording.

    def append_data(self, data_str: str) -> None:
        """
        Converts a string from the loggy into a list of floats and
        appends it to the main list.
        If recording is enabled, the data will also be recorded.
        This function will calculate the resistive temperature if required.
        data_str: "D:CH1,CH2,CH3,CH4,CH5,CH6,CH7,CH8"
        """
        if data_str.count(',') != 7:
            return  # skip the line if it does not follow the protocol
        data_str = data_str[2:]  # Remove the "D:"
        data_str_list = data_str.split(',')
        now = time.time()
        self._data_list[0].append(now - self._start_time)
        self._data_list[0] = self._data_list[0][-1000:]

        for channel, dat_str in enumerate(data_str_list, start=1):
            val = float(dat_str)
            if channel in VOLT_CHANNELS:
                if "(C)" in self.headers[channel]:
                    if "200" in self.headers[channel]:
                        current = 0.000200  # 200uA
                    else:
                        current = 0.000010  # 10uA
                    if val < 0:
                        val *= -1
                    rt = val / current
                    if "PT1000" in self.headers[channel]:  # °C PT1000 200uA
                        # if this is negative GUI will fail
                        val = -0.287154 * math.sqrt(abs(159861899 - 21000 *
                                                        rt))
                        val += 3383.81
                    else:  # °C Thermistor 200uA
                        ln = math.log(rt / 1000)
                        val = (A_THERM
                               + B_THERM * ln
                               + C_THERM * ln ** 2
                               + D_THERM * ln ** 3) ** -1
                        val -= 273.15  # convert kelvins to celcius
            self._data_list[channel].append(val)
            self._data_list[channel] = self._data_list[channel][-1000:]

    def clear_data(self) -> None:
        """This function will remove all the data from the
         _data_list and the _save_list"""
        self._start_time = time.time()
        self._data_list = [[] for _ in range(9)]
        self._save_list = [[] for _ in range(9)]

    def get_data(self) -> list:
        """This function returns the entire _data_list.
        This function should be called every 200ms."""
        if self._is_data_recording:
            self._save_list[0].append(time.time())
            for i in CHANNELS_LIST:
                self._save_list[i].append(self._data_list[i][-1])
        return self._data_list

    def ready_to_plot(self) -> int:
        """This function returns 0 if not ready to plot and
        1 if ready to plot"""
        return self._ready_to_plot


class WriteLines(st.LineReader):
    """Class is used to handle a reader thread to read in lines sent from
    firmware to the GUI."""

    def __init__(self, callback, root: tk.Frame | tk.Tk):
        """
        Parameters
        ----------
        callback :
            A callback function used whenever the LineReader recieves a
            message.
        """
        super().__init__()
        self._callback = callback
        self._control_frame = root

    def connection_made(self, transport):
        """Function used to initialise the LineReader. Mostly inherited
        from the super class, with a message printed to the terminal indicating
        startup.
        Returns nothing.
        """
        super(WriteLines, self).connection_made(transport)

    def handle_line(self, data):
        """
        Function is called whenever the Line Reader reads in data sent from the
        port.
        Parameters
        ----------
        data:
            The recieved data from the firmware.
        """
        self._callback(data)

    def connection_lost(self, exc):
        """Function prints a message to the terminal when the connection with
        the Oirt ceases.
        """

        sys.stdout.write("error message\n")
        message = "port closed"
        errors.put(message)

        pass


def search_for_point(x_coordinate, xdata) -> int:
    """
    This function will iterate through all the points in xdata, and it will
    return the index of the point in xdata.
    that is closest to x_coordinate
    """
    difference = sys.maxsize  # Larges value of a integer
    idx = 0

    for i, num in enumerate(xdata):
        diff = abs(num - x_coordinate)
        if diff < difference:
            difference = diff
            idx = i
    return idx
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

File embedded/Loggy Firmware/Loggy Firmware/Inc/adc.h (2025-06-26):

/*
 * adc.h
 *
 * Created: 2025/3/26 14:53:17
 *  Author: Zhe Gao
 */

#ifndef ADC_H_
#define ADC_H_

#include "eeprom.h"
#include <avr/interrupt.h>
#include <avr/io.h>
#include <stdint.h>
#include <stdio.h>
#include <string.h>

// address of ADS1115 chip
#define ADC_ADDRESS_1 0x49
#define ADC_ADDRESS_2 0x48

// basic setting for chip
#define ADDR_CONV 0
#define ADDR_CONF 1
#define ADDR_LOWTHRESH 2
#define ADDR_HIGHTHRESH 3
#define ADC_CONF_OS 0x8000
#define ADC_CONF_MUX1 0x0000
#define ADC_CONF_MUX2 0x3000
#define ADC_CONF_PGA 0x0600
#define ADC_CONF_MODE 0x0000
#define ADC_CONF_DR 0x00E0

// The constant value to calculate the temp
#define ADC_10_RESOLUTION 1023.0
#define TEMP_ADC_V 3.3
#define RESISTER_VALUE 12253.0
#define BETA_CONSTANT 1.0
#define BETA_TEMP_VALUE 3380
#define BETA_TEMP_25_NORMAL 298.15
#define BETA_TEMP_0_NORMAL 273.15
#define BETA_NORMAL_TEMP_VALUE 10000

// number of formula to calculate the vol
#define ADC_GAIN 10
#define ADC_DIVI 9.98
#define ADC_1_VREF 1.65
#define ADC_10_VREF 16.5
#define ADC_SCALE 1.024
#define ADC_16_RESOLUTION 32768.0

#define ADC_CALC_1V_SCALE_CHAN2_4(adc)                                \
    ((ADC_GAIN * (ADC_1_VREF + ((adc)*ADC_SCALE / ADC_16_RESOLUTION)) \
         - ADC_10_VREF)                                               \
        / ADC_DIVI)

#define ADC_CALC_10V_SCALE_CHAN2_4(adc)                              \
    (ADC_GAIN * (ADC_1_VREF + ((adc)*ADC_SCALE / ADC_16_RESOLUTION)) \
        - ADC_10_VREF)

#define ADC_CALC_1V_SCALE_CHAN1_3(adc)                                \
    ((ADC_GAIN * (ADC_1_VREF - ((adc)*ADC_SCALE / ADC_16_RESOLUTION)) \
         - ADC_10_VREF)                                               \
        / ADC_DIVI)

#define ADC_CALC_10V_SCALE_CHAN1_3(adc)                              \
    (ADC_GAIN * (ADC_1_VREF - ((adc)*ADC_SCALE / ADC_16_RESOLUTION)) \
        - ADC_10_VREF)

extern Config LoggyConfig;

int16_t read_adc_channel(uint8_t addr);

void select_adc_channel(uint8_t addr, uint16_t config);

void get_vol_values(SensorData* data, Config* loggy_config);

void adc_init(void);

uint16_t read_adc(void);

void wait_adc_chip1();

void wait_adc_chip2();

void get_temp_value(float* temp);

#endif /* INCFILE1_H_ */

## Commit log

2025-05-22 Add BOM and most recent schematic PDF
    [ENGG2800 BOM (2).xlsx]
2025-05-22 Add copper layers of PCB to output pdf
2025-05-22 Add most recent PCB and individual PCB and schematic PDFs
    [ADC and IMU.SchDoc, ADC.SchDoc, ATmega328p.SchDoc, Accelerometer.SchDoc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]
2025-05-23 Add most recent version of stuff
    [ADC.SchDoc, ATmega328p.SchDoc, Accelerometer.SchDoc, Alarms and Buttons.SchDoc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]
2025-06-26 Add most recent code and PCB
    [2025-06-23_17-01-37.csv, ENGG2800 BOM (2).xlsx, Loggy Bottom.stl, Loggy Top Proj.3mf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]
2025-06-26 Add images
    [2025-06-26_16-49-01.csv]
2025-06-26 Remove csv files from lab_pc directory
    [2025-06-23_17-01-37.csv, 2025-06-26_16-49-01.csv]
